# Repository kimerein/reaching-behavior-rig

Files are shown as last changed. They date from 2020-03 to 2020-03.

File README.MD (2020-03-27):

This repo contains hardware and software files for building and operating a behavior rig that dispenses food pellets to a mouse. 
The food pellets are positioned in front of the mouse by an apparatus containing two stepper motors controlled by an Arduino. 
The mouse sits in the "mouse house" or mouse enclosure to access the food pellets. 
There is a gap between the "mouse house" and the mechanism that presents food pellets, so the mouse has to reach for the food pellet with the forelimb and forepaw.
Pellet orientation is not controlled during loading or pellet presentation to the mouse. 
The rig is designed to maneuver 20 mg food pellets. 

# Useful Info. and Answers to FAQs

* **This is for scientists.**
* **This is a behavior rig that presents food pellets to a mouse.**
* **The components of the rig are controlled by an Arduino.**
* **This is for scientists interested in studying forelimb reaching behaviors in mice, designed by a neuroscientist.** 
* **This repo contains materials related to my post-doctoral work.** 
Note: I am a scientist, not an engineer. 
Certainly, there are non-optimal components of this design. 
This is not fancy. Yes, one step is to glue on a paintbrush.
Please feel free to improve upon and share this design, but ...
* **Please acknowledge this Github page in any publications relying on or adapting this design. Thank you!**
* **This is DIY and use-at-your-own-risk material.** 
You will need to adapt the code and designs to your own goals.
I cannot answer support requests.
Building this rig based on these materials requires a decent understanding of Arduino, ThorLabs parts, and generally good spatial reasoning.
* **Known Issues**
This rig works well for my needs. I run this rig for 5 hours per day without jammed pellets. 
However, there are several caveats.
First, the rig does not work well unless all components are exactly properly positioned and very well-secured.
Second, mis-loading of pellets does occur. This occurs for about 1 in 50 pellets (e.g., pellet is not in the proper position when presented to the mouse or pellet is missing).
Third, jammed pellets are infrequent, but this does occur. Usually, I observe jammed pellets only when a screw is loose or a rig component is improperly positioned.
The rig requires periodic maintenance.
Note that commercial food hoppers (pellet dispensers) do exist. 
* **Food pellets**
This rig was designed to dispense 20 mg food pellets from Bio-Serv (e.g., F05301).

# Contributors

https://github.com/kimerein/

https://github.com/marciiadarola/

# Parts List

Only the top 2 sections of this list, "Components for maneuvering pellets" and "Arduino components", contain components required to build the behavior rig.
I use the other components for other features.

[Parts List](./parts_list.csv)

## Notes on 3D-printed parts

These are the 3D-printed parts:

[Pellet loader container](./parts/pellet_loader_container.stl)

[Pellet loader conical piece](./parts/pellet_loader_conical_piece.stl)

[Chute and blocker (these two mechanisms are combined into one piece)](./parts/chute_and_blocker.stl)

[Perch rings to fit around ThorLabs posts](./parts/perch_rings.stl)

[Perch middle piece, where mouse's forepaws rest, should be cut to correct size and fit into 2 perch rings](./parts/perch_connector.stl)

I've also included the .ipt versions of these .stl files, in case you want to modify the designs with CAD.

I printed these pieces using Black V4 resin on a Form 2 FormLabs printer, but other resins and printers should work.

## Notes on laser-cut parts

These are the parts cut out of acrylic sheets, saved as Adobe Illustrator files:

[One file including all of the parts to be cut from 1/8 inch black acrylic](./parts/behaviorBox_with_pellet_presenter.ai)

[Pellet presenter wheel alone](./parts/pellet_presenter_wheel.ai)

[Pellet loader parts to be cut from 1/16 inch clear acrylic](./parts/loader_two_plastic_parts.ai)

Note that the pellet presenter wheel has raster engraving (black filled sections). All other lines indicate clean cuts through the acrylic.

The file [with labels](./parts/behavior_box_parts_with_labels.ai) is not for laser cutting. It is instructional only and includes labels on the pieces.

# Building Reaching Rig

[How to build rig](./BUILDRIG.MD)

# Control code for Arduino

An example of the Arduino code that I use to control the behavior box is in this repo. 
Note that you may need to debug the code with your behavior box.
In particular, be aware that, if Arduino turns on a pull-up resistor, the HIGH and LOW states will be flipped for certain pin outs.

# Instructions

First, you should have a clear understanding of your experimental needs. 
Use these materials as a starting point for finding your own solutions and approach.
You will need to adapt/problem-solve depending on your goals.

# How to Help

In the spirit of open-source science, please publish your own improvements and updates to Github. Happy experimenting!

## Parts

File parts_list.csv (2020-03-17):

Material | Description | Vendor | Part # | # needed | Link
Components for maneuvering pellets:
Bipolar Stepper Motor 200 Step 0.35A 12VDC | stepper motor | Digi-Key | 1528-1062-ND | 2 | https://www.digikey.com/product-detail/en/324/1528-1062-ND/5022791?WT.mc_id=IQ_7595_G_pla5022791&wt.medium=cpc&wt.srch=1
Black Scratch-Resistant Acrylic 24 x 24 inches | black acrylic for laser cutter | McMaster-Carr | 8505K744 | 1 | https://www.mcmaster.com/8505k744-8505K143
Access to 3D printer | 3D printing (see .stl files) | Harvard Instrumentation Core
Access to laser cutter | laser cut black acrylic (see .ai files) | Harvard Instrumentation Core
Ø1/2" Post Holder, Spring-Loaded Hex-Locking Thumbscrew, L = 1.5" | structure | ThorLabs | PH1.5 | 3 | https://www.thorlabs.com/thorproduct.cfm?partnumber=PH1.5#ad-image-0
PH1 - Ø1/2" Post Holder, Spring-Loaded Hex-Locking Thumbscrew, L = 1" | structure | ThorLabs | PH1 | 2 | https://www.thorlabs.com/thorproduct.cfm?partnumber=PH1#ad-image-0
BA1S - Mounting Base, 1" x 2.3" x 3/8" | structure | ThorLabs | BA1S | 5 | https://www.thorlabs.com/thorproduct.cfm?partnumber=BA1S
BA1 - Mounting Base, 1" x 3" x 3/8" | structure | ThorLabs | BA1 | 2 | https://www.thorlabs.com/thorproduct.cfm?partnumber=BA1
DTS50 - 2" Dovetail Translation Stage, 1/4"-20 Taps | structure | ThorLabs | DTS50 | 2 | https://www.thorlabs.com/thorproduct.cfm?partnumber=DTS50
PH2 - Ø1/2" Post Holder, Spring-Loaded Hex-Locking Thumbscrew, L = 2" | structure | ThorLabs | PH2 | 4 | https://www.thorlabs.com/thorproduct.cfm?partnumber=PH2#ad-image-0
TR2 - Ø1/2" Optical Post, SS, 8-32 Setscrew, 1/4"-20 Tap, L = 2" | structure | ThorLabs | TR2 | 7 | https://www.thorlabs.com/thorproduct.cfm?partnumber=TR2
TR1 - Ø1/2" Optical Post, SS, 8-32 Setscrew, 1/4"-20 Tap, L = 1" | structure | ThorLabs | TR1 | 4 | https://www.thorlabs.com/thorproduct.cfm?partnumber=TR1
TR3 - Ø1/2" Optical Post, SS, 8-32 Setscrew, 1/4"-20 Tap, L = 3" | structure | ThorLabs | TR3 | 3 | https://www.thorlabs.com/thorproduct.cfm?partnumber=TR3
PH3 - Ø1/2" Post Holder, Spring-Loaded Hex-Locking Thumbscrew, L = 3" | structure | ThorLabs | PH3 | 1 | https://www.thorlabs.com/thorproduct.cfm?partnumber=PH3#ad-image-0
DC Power 12V 5.5mm Barrel Connector Female To Pigtail Bare Wires | power to monitor, auxiliary motor shield power, camera power | Amazon | B00E0O2BWC | 3 | https://www.amazon.com/Power-Barrel-Connector-Female-Pigtail/dp/B00E0O2BWC
Zip ties |  | general lab supplies
Kwik-Sil | securing motors with help of motor positioners | WPI | KWIK-CAST | 1 | https://www.wpiinc.com/products/top-products/kwik-cast-kwik-cast-sealant
Dental cement | e.g., Metabond | general lab supplies
Fast-drying glue | e.g., Loctite with Zipkicker catalyst | general lab supplies
Arduino project enclosure | securing Arduino | SparkFun | PRT-10088 | 1 | https://www.sparkfun.com/products/10088
Extension cords and power strip |  | general lab supplies
12 V power source | for Arduino, monitor, DVR and V2 motor shield auxiliary power | general lab supplies |  | 4
5 V power source | for camera | general lab supplies |  | 1
MB8 - Aluminum Breadboard 8" x 8" x 1/2", 1/4"-20 Taps | 1 plate for mouse enclosure, 1 plate for pellet presentation apparatus (Note that I decouple these two pieces to prevent transference of motor vibrations to mouse) | ThorLabs | MB8 | 2 | https://www.thorlabs.com/thorproduct.cfm?partnumber=MB8
AP90 - Right-Angle Mounting Plate, 1/4"-20 Compatible | attaches mouse enclosure to translation stage | ThorLabs | AP90 | 2 | https://www.thorlabs.com/thorproduct.cfm?partnumber=AP90
CL2 - Heavy-Duty Variable Height Clamp, 1/4"-20 Tapped | structure | ThorLabs | CL2 | 3 | https://www.thorlabs.com/thorproduct.cfm?partnumber=CL2
XT95P12 or other mounting plate | structure | ThorLabs | XT95P12 | 1 | https://www.thorlabs.com/thorproduct.cfm?partnumber=XT95P12
BA2 - Mounting Base, 2" x 3" x 3/8" | structure | ThorLabs | BA2 | 2 | https://www.thorlabs.com/thorproduct.cfm?partnumber=BA2
1/4-20 and 8-32 screws, washers and nuts |  |  |  | many
DC Power 12V 5.5mm Barrel Connector Female To Pigtail Bare Wires | for connecting powered components, including auxiliary power to Arduino motor shield | Amazon | B00E0O2BWC | 4 | https://www.amazon.com/Power-Barrel-Connector-Female-Pigtail/dp/B00E0O2BWC
Thorlabs 6 mm rods for pellet loader | for positioning pellet loader 3D-printed pieces | Thorlabs | ER6 | 2 | https://www.thorlabs.com/thorproduct.cfm?partnumber=ER6
Thorlabs holder for 6 mm rods | for positioning pellet loader 3D-printed pieces | Thorlabs | CP02B | 2 | https://www.thorlabs.com/thorproduct.cfm?partnumber=CP02B
Clear Cast Acrylic Sheet, 12" x 12" x 1/16" | for pellet loader wheel and bottom piece of pellet loader | McMaster-Carr | 8560K171 | 1 | https://www.mcmaster.com/catalog/125/3732
Princeton Best Synthetic Sable Brush - Round, Short Handle, Size 3 | for brushing off pellets | Blick | Item #:06170-1003 | 1 | https://www.dickblick.com/items/06170-1003/
Arduino components, including components for logging Arduino actions:
Arduino Uno R3 | microcontroller | Adafruit | PID: 50 | 1 | https://www.adafruit.com/product/50
Adafruit V2 motor shield, v2.3 | for controlling 2 stepper motors | Adafruit | PID: 1438 | 1 | https://learn.adafruit.com/adafruit-motor-shield-v2-for-arduino/overview
Proto-Screwshield (Wingshield) R3 Kit for Arduino | for securely attaching in/out | Adafruit | PID: 196 | 1 | https://www.adafruit.com/product/196
Shield stacking headers for Arduino (R3 Compatible) | for stacking shields | Adafruit | PRODUCT ID: 85 | 4 | https://www.adafruit.com/product/85?gclid=EAIaIQobChMIvciagNr31AIVl0sNCh3qLgy1EAQYASABEgL-u_D_BwE
Arduino Ethernet Shield 2 | for writing Arduino output data to micro-SD card during experiment | SparkFun | DEV-11166 | 1 | https://www.sparkfun.com/products/11166
Components for video recording of mouse behavior (30 fps):
Weatherproof TTL Serial JPEG Camera with NTSC Video and IR LEDs | for infra-red (IR) video in behavior box | Adafruit | 613 | 1 | https://www.adafruit.com/product/613
SanDisk microSDHC 32GB Flash Memory Card, Black, SDSDQM-032G-B35 | micro-SD card for Arduino output storage | Amazon | B004G60AD6 | 1 | https://www.amazon.com/SanDisk-microSDHC-Memory-SDSDQM-032G-B35-Packaging/dp/B004G60AD6
SanDisk 32GB Ultra Class 10 SDHC UHS-I Memory Card Up to 80MB, Grey/Black (SDSDUNC-032G-GN6IN) | SD card for video storage | Amazon | B0143RT8OY | 1 | https://www.amazon.com/SanDisk-Ultra-Class-Memory-SDSDUNC-032G-GN6IN/dp/B0143RT8OY?s=pc
Anysun® Mini Security DVR - Sd Card Recording with Remote Control Sd Slot | DVR for storing video on SD card | Amazon | B00WUPKLPW | 1 | https://www.amazon.com/Anysun%C2%AE-Mini-Security-DVR-Recording/dp/B00WUPKLPW
LEE Filters 3x3" Infra Red #87C Infrared Polyester Filter | for ensuring that only IR light (not red light) exits IR LEDs -- mouse cannot see IR | BandH | B&H # LE87C33 | 1 | https://www.bhphotovideo.com/c/product/292664-REG/LEE_Filters_87CP3_3_x_3_Infrared.html
N-BK7 Plano-Convex Lens, Ø1", f = 150.0 mm, Uncoated | for camera | ThorLabs | LA1433 | 1 | https://www.thorlabs.com/thorproduct.cfm?partnumber=LA1433
Black and red wires | wiring electronics
Other (optional):
X-mini WE micro portable NFC Bluetooth smartphone capsule speaker, XAM17-GM-B | play sound of motors turning all the time, to mask actual motor turning | Amazon | B00I6BJ592 | 2 | https://www.amazon.com/X-mini-portable-Bluetooth-smartphone-XAM17-GM-B/dp/B00I6BJ592
Liztek 40W/8A 5-Port USB Charger Desktop Charger Charging Station with SmartLiz Technology (Black) | for charging speakers | Amazon | B00R6MJ7UO | 1 | https://www.amazon.com/Liztek-Charger-Charging-SmartLiz-Technology/dp/B00R6MJ7UO?s=kitchen
UGREEN 3.5mm Male to Female Extension Stereo Audio Extension Cable Adapter Gold Plated Compatible for iPhone, iPad or Smartphones, Tablets, Media Players | audio to speakers | Amazon | B00LM4OMUW | 1 | https://www.amazon.com/UGREEN-Extension-Adapter-Compatible-Smartphones/dp/B00LM4OMUW
Belkin Speaker and Headphone Splitter | audio to speakers | Amazon | B000067RC4 | 1 | https://www.amazon.com/Belkin-Speaker-and-Headphone-Splitter/dp/B000067RC4?th=1
Camecho Universal 7 inch Car Vehicle RearView reversing color Monitor 2 Video Input & High Resolution Rotating TFT LCD Screen with Remote Control and Mounting Bracket | for watching mouse in behavior rig, in real-time | Amazon | B00MQF9P12 | 1 | https://www.amazon.com/Camecho-Universal-RearView-reversing-Resolution/dp/B00MQF9P12?s=electronics
Interlock magnetic switch | for determining when behavior rig door is open | Amazon | B0009SUF08 | 1 | https://www.amazon.com/Directed-Electronics-8601-Magnetic-Switch/dp/B0009SUF08
Velcro Tape 3/4"Wx15' Sticky Back Black Boxed | for attaching acoustic foam to inside of behavior box | Amazon | B01MTKKG33 | 1 | https://www.amazon.com/Velcro-Tape-Sticky-Black-Boxed/dp/B01MTKKG33?s=office-products
Custom machined headframe holders |  | Harvard Machine Shop |  | 1 pair
Optional: components for optogenetics, including manipulator for fiber placement, wire to BNC, etc. |  | general lab supplies
Blue LED and resistor | LED distractor | general lab supplies
Black tape |  | general lab supplies
99% Blackout Window Curtain Panel Grommet Top Drapes 2 Panel Set Room Darkening Thermal Insulated Blackout Drapes for Bedroom (W52 x L84,Black) | for covering behavior box during behavior (mouse needs to be completely in the dark) | Amazon | B01N0T12O6 | 1 | https://www.amazon.com/Blackout-Curtain-Grommet-Darkening-Insulated/dp/B01N0T12O6?s=furniture
Magnetic Latch for 1" and 1-1/2" High Aluminum T-Slotted Framing Extrusion | holding door closed | McMaster-Carr | 47065T165 | 1 | https://www.mcmaster.com/#catalog/123/1948/=1a31q14
Rail-to-Panel Hinge for 1" High Rail, Black OR 201590 Sea-Dog Line Offset Butt Hinge Stainless Steel 1-1/2" X 1-1/2" Inch | hinge for behavior box door | McMaster-Carr or Amazon | https://www.mcmaster.com/47065t162 OR B00U1TJOZC | 2 pairs | https://www.amazon.com/201590-Sea-Dog-Line-Offset-Stainless/dp/B00U1TJOZC | https://www.mcmaster.com/47065t162
Optional: Clay for blocking light from exiting fiber (if doing optogenetics)
Optional: rotary encoders for measuring wheel positions
Optional: NogaFlex Holder - Model: NF1022 | Flexible arm for positioning optical fiber for optogenetics, for positioning air tubing | Amazon | B002NERHSO | 1 | https://www.amazon.com/Noga-NogaFlex-Holder-Model-NF1022/dp/B002NERHSO?s=industrial
Optional: 8 inch ThorLabs post holder for positioning Noga arm | For holding Noga arm
FC/FC General Purpose POF Patch Cords, 1.00 m 1.0 mm plastic optical core, polyethylene 2.2 mm jacket, 1.00 m | for optogenetic stimulation of superficial cortical regions | Industrial Fiber Optics | IF 181L-1-0 | 1 or more | http://i-fiberoptics.com/patchcord-detail.php?series=181L&stock_number=IF%20181L-1-0&summaryrow=12
316 Stainless Steel Dowel Pins | for raising behavior rig and adding pellet collecting drawers | McMaster-Carr | 97395A616 | 4 | https://www.mcmaster.com/#standard-dowel-pins/=1ac8p06
Ø1.5" Mounting Post, 1/4"-20 Taps, L = 1" | for raising behavior rig and adding pellet collecting drawers | Thorlabs | P1 | 4 | https://www.thorlabs.com/thorproduct.cfm?partnumber=P1
Rail aluminum T-slotted framing extrusion, triple profile | 24 inches | McMaster-Carr | 47065T511 | 3 | https://www.mcmaster.com/47065t511
Rail aluminum T-slotted framing extrusion, single profile | 24 inches | McMaster-Carr | 47065T101 | 7 | https://www.mcmaster.com/47065t101
Aluminum T-slotted framing extrusion, 6 inch brace | 6 inches, 1 inch thick | McMaster-Carr | 47065T186 | 12 | https://www.mcmaster.com/47065t186
Rail aluminum T-slotted framing extrusion, single profile, cut-to-length OR cut the length yourself | 28 inches | McMaster-Carr | 47065T801 | 4 | https://www.mcmaster.com/47065t801
Corner flush 90 deg angle surface bracket for single rails | smallest size | McMaster-Carr | 3136N157 | 10 | https://www.mcmaster.com/3136n157
Drop-in fasteners | spring-loaded for staying in place in vertical rails | McMaster-Carr | 47065T226 | 20 | https://www.mcmaster.com/47065t226
Snap-in mounting plate | for holding black acrylic coverings | McMaster-Carr |  | 9
Egg crate sound-proofing | 3 inches thick, 54 x 54 inches | McMaster-Carr | 9710T66 | 3 | https://www.mcmaster.com/9710T66
Sensor holder drop-in fastener | spring-loaded | McMaster-Carr | 5537T352 | 10 | https://www.mcmaster.com/5537t352
Black acrylic | 24 x 24 inches | McMaster-Carr | 8505K744 | 5 | https://www.mcmaster.com/8505k744-8505K143
Black Cast Acrylic Sheet 24" x 36" x 1/8" | 36 x 48 inches | McMaster-Carr | 8505K745 | 1 | https://www.mcmaster.com/8505k745-8505K153
Full Size Clear Polycarbonate Food Pan - 2 1/2" Deep | for collecting dropped food pellets underneath the behavior rig | WebstaurantStore | 700PLPA8002 | 2 | https://www.webstaurantstore.com/full-size-clear-polycarbonate-food-pan-2-1-2-deep/700PLPA8002.html

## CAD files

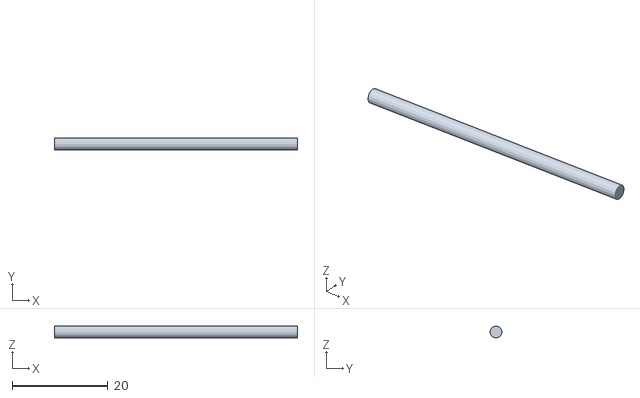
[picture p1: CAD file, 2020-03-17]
parts/perch_connector.stl
50.8 x 2.50 x 2.50

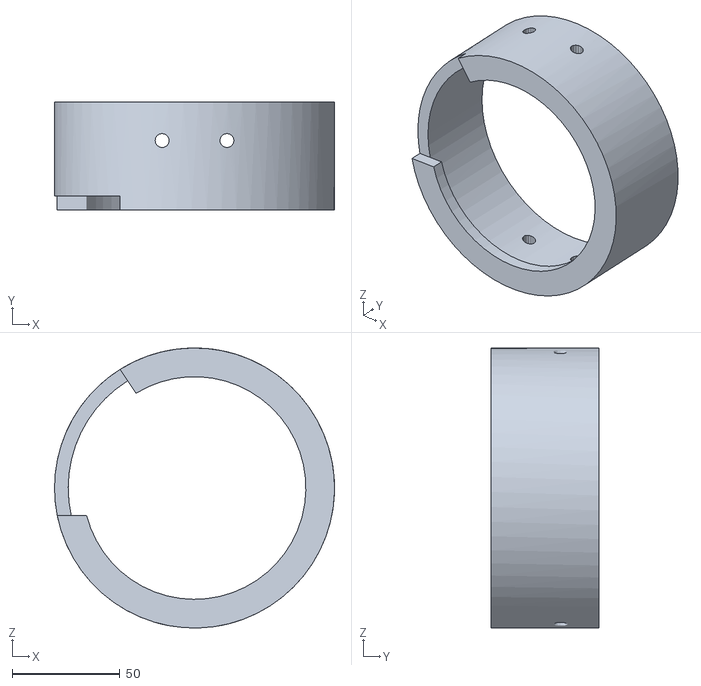
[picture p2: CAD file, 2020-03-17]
parts/pellet_loader_container.stl
129.7 x 49.8 x 129.7

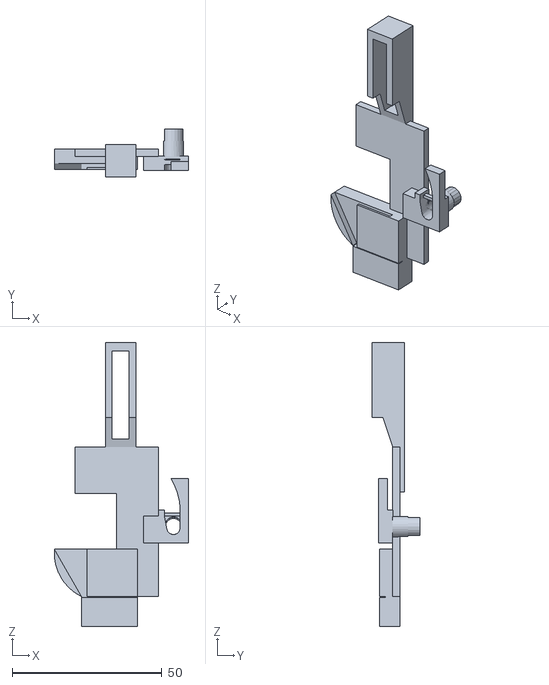
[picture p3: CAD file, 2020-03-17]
parts/chute_and_blocker.stl
44.9 x 16.2 x 94.9

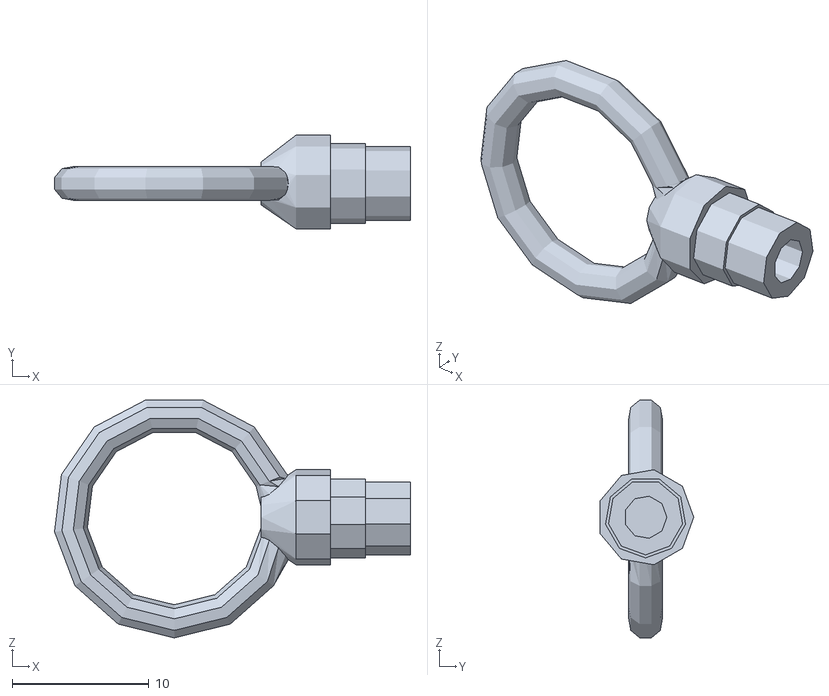
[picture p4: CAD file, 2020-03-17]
parts/perch_rings.stl
26.0 x 6.85 x 17.4

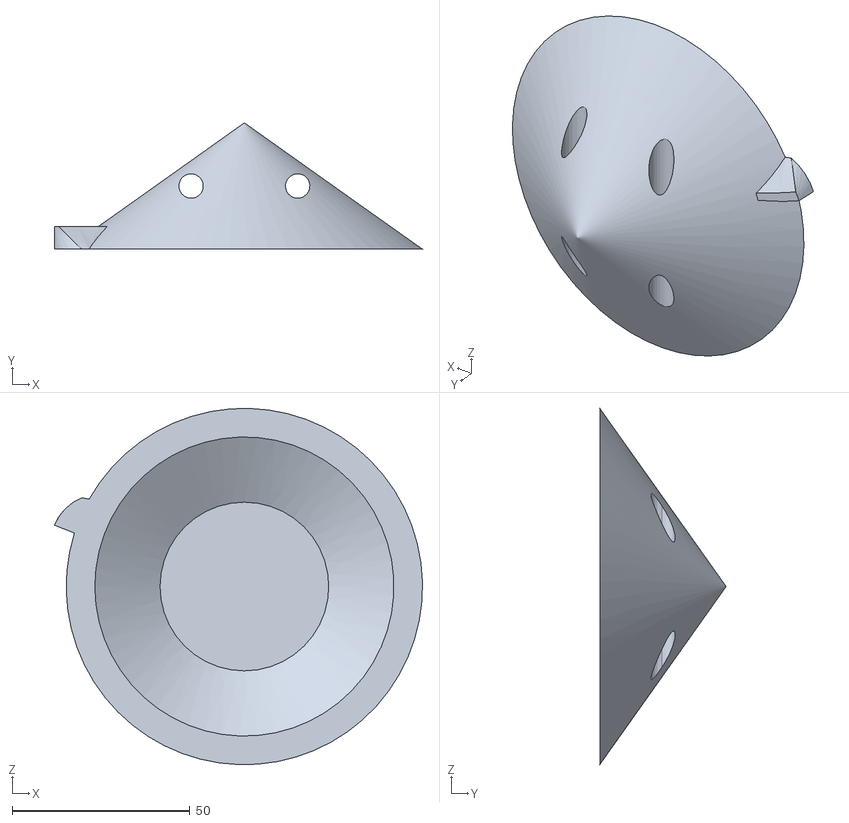
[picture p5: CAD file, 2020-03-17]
parts/pellet_loader_conical_piece.stl
103.6 x 35.6 x 100.2

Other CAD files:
parts/chute_and_blocker.ipt
parts/pellet_loader_conical_piece.ipt
parts/pellet_loader_container.ipt
parts/perch_connector.ipt
parts/perch_rings.ipt

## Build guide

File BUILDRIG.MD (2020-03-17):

# Building Reaching Rig

1. Build frame (McMaster Aluminum T-Slotted Framing Extrusion, see Materials List for sizes). 
2. 3D print .stl files. I used Black V4 resin with a FormLabs 2 printer, but other printers and resins should work.
3. Laser cut .ai files. Note that the pellet presenter wheel has raster engraved sections (black fill). For all other lines (red), cut all the way through the acrylic sheet.
4. NOTE: Build the two halves of the behavior rig separately. We will then attach these two pieces to the box frame. Build: A. Pellet Disks Apparatus and B. Mouse House Apparatus on two separate breadboards. (This separation prevents transmission of the stepper motor vibrations to the mouse.) Optional: 3rd micrometer for up-down movement of mouse. Note that this rig could be built excluding all the micrometers (to save money), but I prefer to include at least 2 micrometers to increase positioning flexibility. 
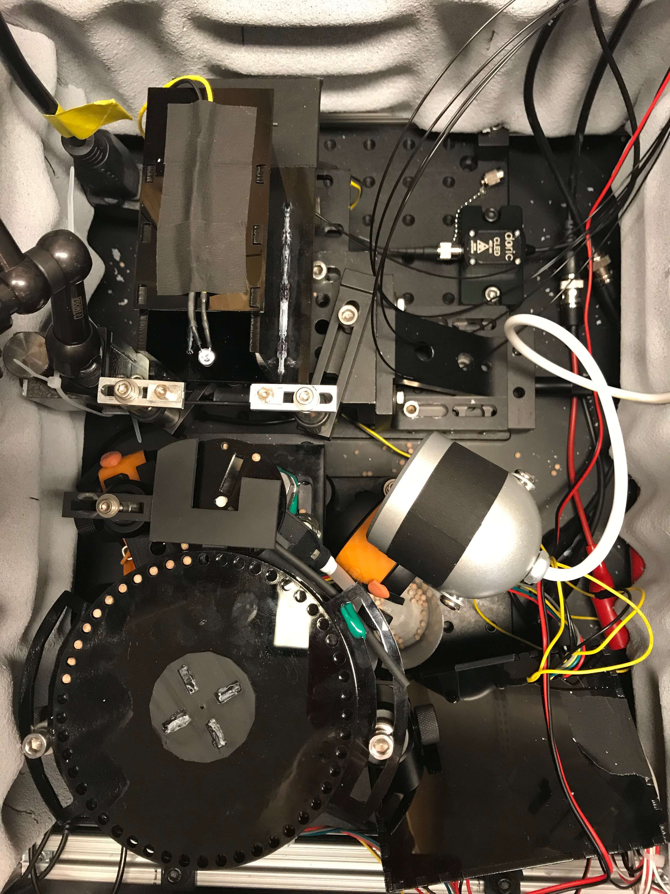
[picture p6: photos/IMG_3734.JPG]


[Two halves of rig from above](./photos/IMG_3734.JPG)

5. **BUILD PELLET DISKS APPARATUS**
6. Assemble raised micrometer platforms. Use appropriate Thorlabs posts and post holders to ensure that the height of Pellet Disks Apparatus matches the height of Mouse House Apparatus. 
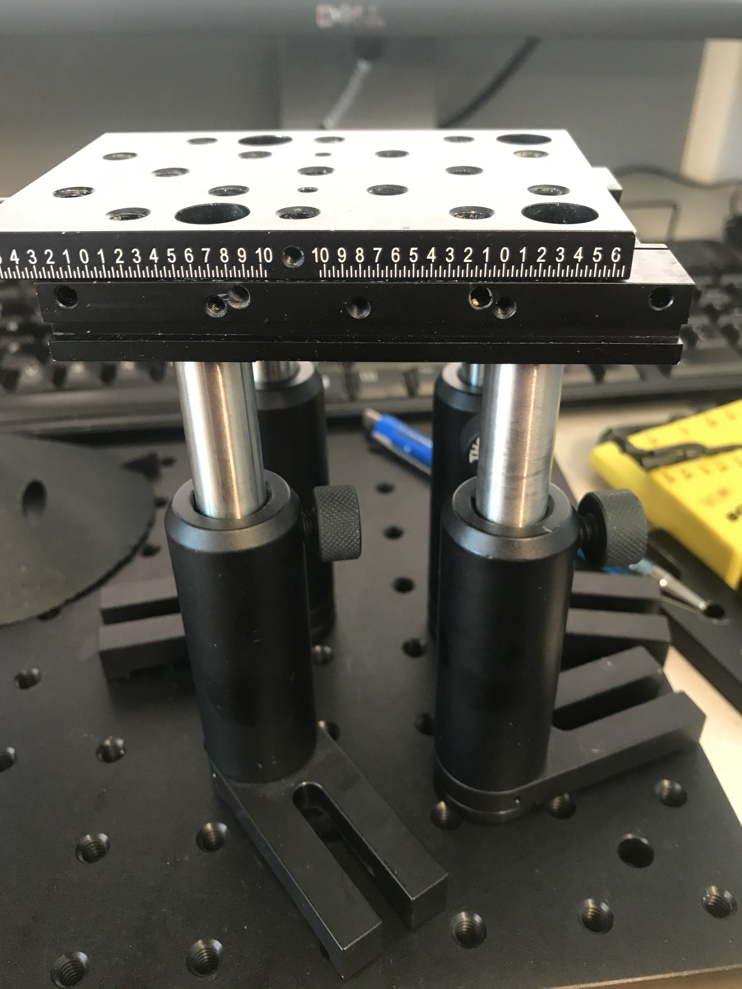
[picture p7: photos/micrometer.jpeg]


[Raised micrometer](./photos/micrometer.jpeg)

7. Build mechanism to present food pellets. These plastic disks maneuver the food pellets. (Think: lazy susan.) There are 2 circular plastic disks. Each is secured to a stepper motor, which enables the disk to spin. The first (smaller) disk presents food pellets to the mouse. The second (larger) disk loads food pellets onto the first (smaller) disk. I call this first disk the “pellet presenter wheel”, and I call the second disk the “loader wheel”. Attach each circular disk to the top of a stepper motor shaft: Hold the plastic disk in place with quick-drying glue (e.g., Loctite/Zipkicker catalyst), then further secure this attachment for permanent hold using dental cement. There is a 3D-printed piece that  mates the “loader wheel” (plastic disk with 50 holes around the edge) to the stepper motor shaft. The “loader wheel” (plastic wheel) sits on the top of this 3D-printed piece. 
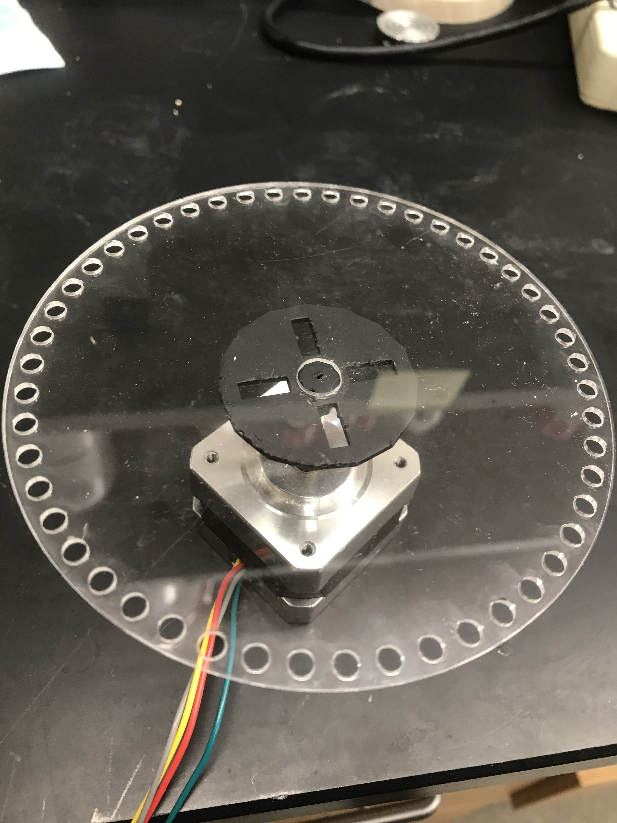
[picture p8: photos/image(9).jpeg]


[Stepper motor, then 3D-printed piece, then loader wheel ](./photos/image(9).jpeg)

The “pellet presenter wheel” should sit directly on top of the motor shaft. Use a leveler to be sure that each wheel is mounted approximately flat with respect to the bottom of the stepper motor base. 

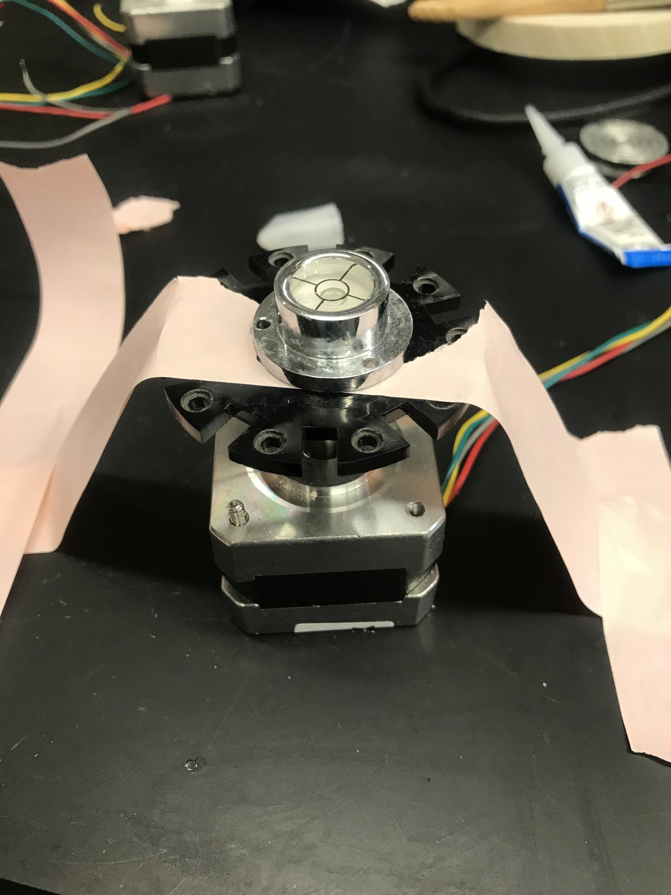
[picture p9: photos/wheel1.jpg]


[Upright attachment method](./photos/wheel1.jpg)

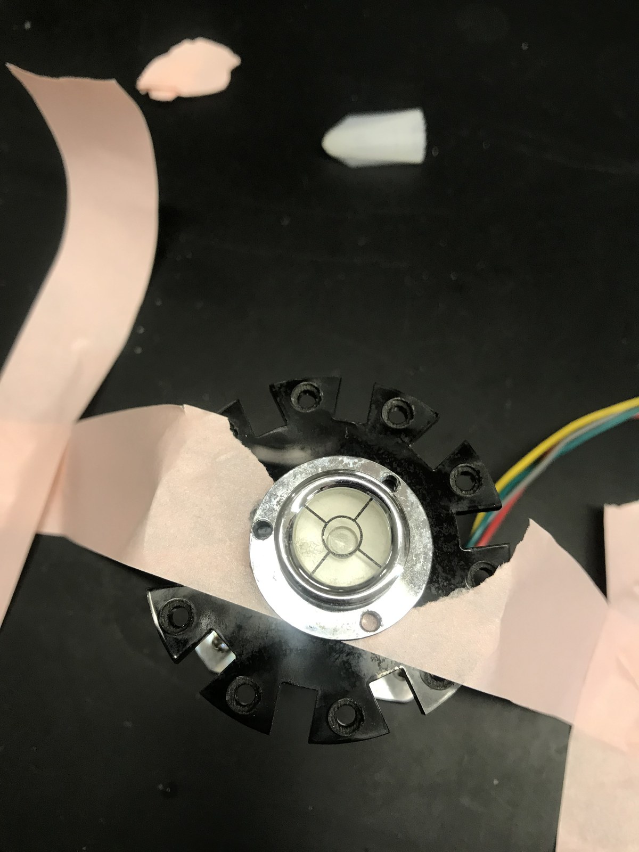
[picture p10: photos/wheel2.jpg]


[Level wheel](./photos/wheel2.jpg)

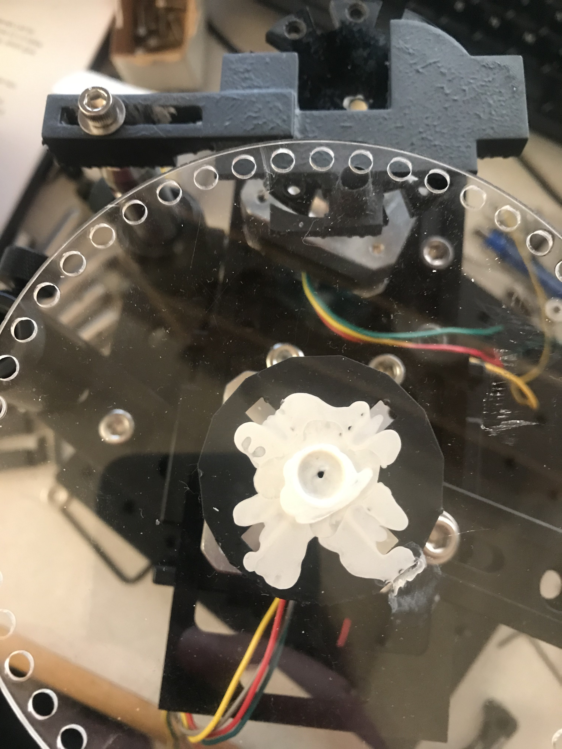
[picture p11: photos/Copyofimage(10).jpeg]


[Pellet loader wheel from above](./photos/Copyofimage(10).jpeg)

8. Use plastic “motor positioners” (plastic stencils) to correctly position the stepper motors on top of the micrometers. Place one motor positioner (black plastic cut-out) on top of the micrometer and screw down loosely. 
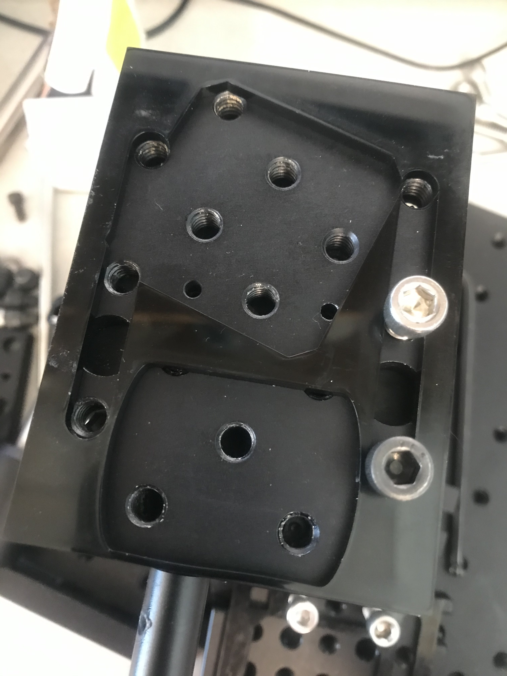
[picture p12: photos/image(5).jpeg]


[“Motor positioner” on micrometer](./photos/image(5).jpeg)

The stepper motor attached to the pellet presenter wheel will sit in this front-most stencil. Attach a small, compatible Thorlabs plate (I used XT95P12, but you can use any compatible piece) to the back of the micrometer, and place the second motor positioner (plastic stencil) on this back plate.

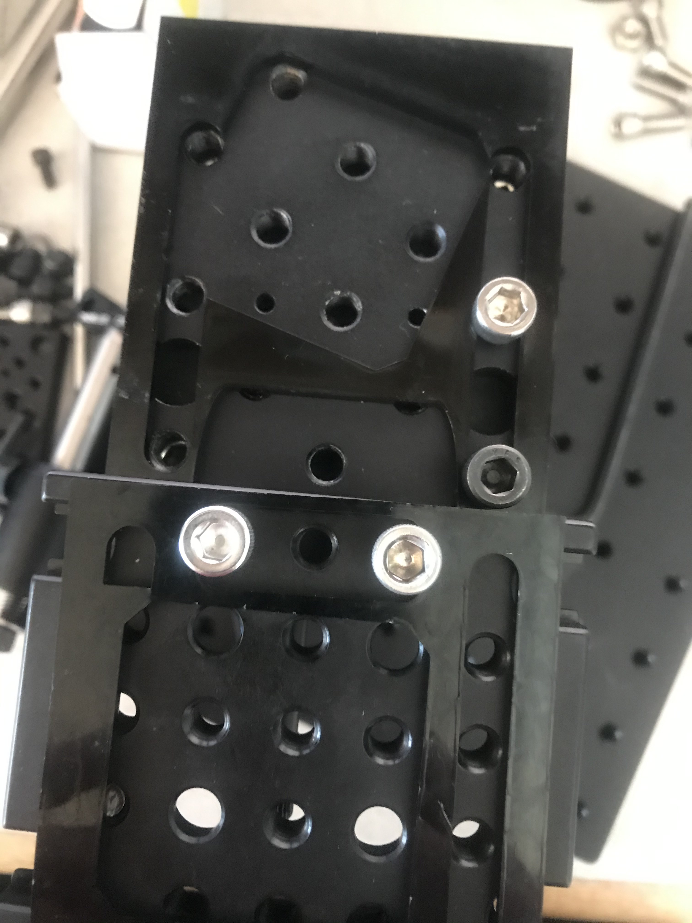
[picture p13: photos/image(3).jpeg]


[Plate and motor positioner for pellet loader](./photos/image(3).jpeg)

The stepper motor attached to the pellet loader sits in this back stencil. Loosely secure motor positioners to the micrometer platforms using screws. Place the stepper motors in the motor positioners.

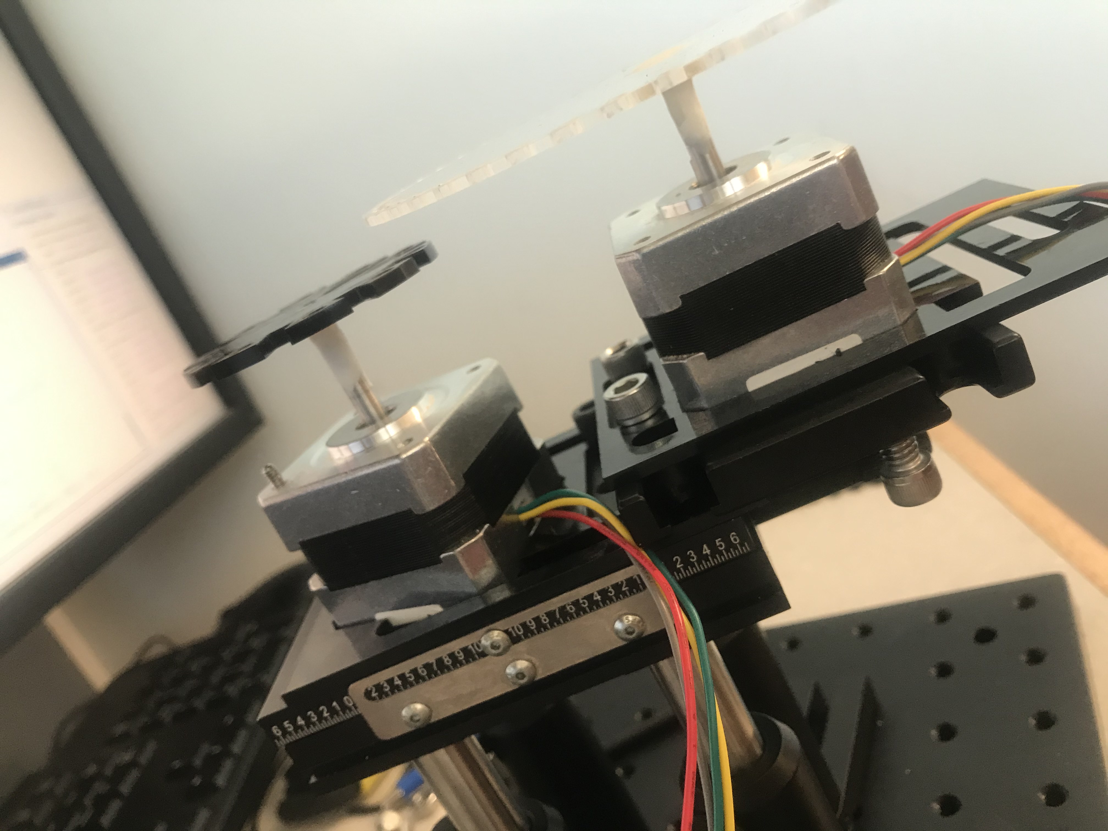
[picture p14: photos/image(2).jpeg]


[With motors](./photos/image(2).jpeg)

9. Gently move the “motor positioners” (plastic stencils) to move the stepper motors. Align the two wheels: a hole in the pellet loader wheel should be aligned directly above a hole in the pellet presenter wheel. 
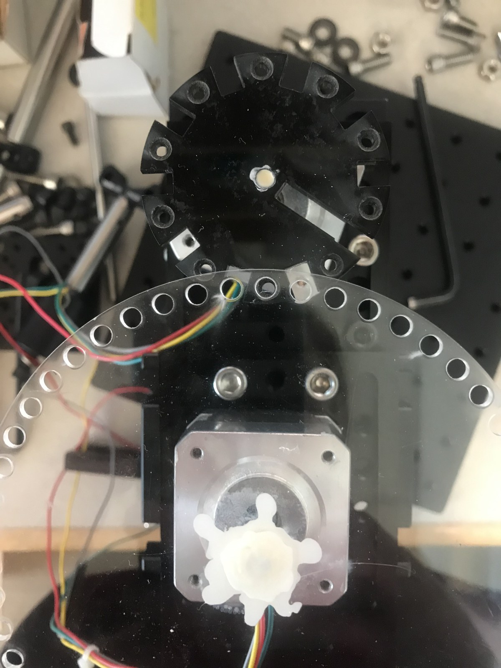
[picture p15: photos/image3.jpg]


[Aligned](./photos/image3.jpg)

Tighten screws. (We will need to adjust this again after plugging in the motors.) Be sure to use screw lengths that do not impede micrometer movements.

10. Build the pellet loader. 

   a. Stack these pieces inside of the large, 3D-printer pellet loader container, in this order: plastic ring with one hole 
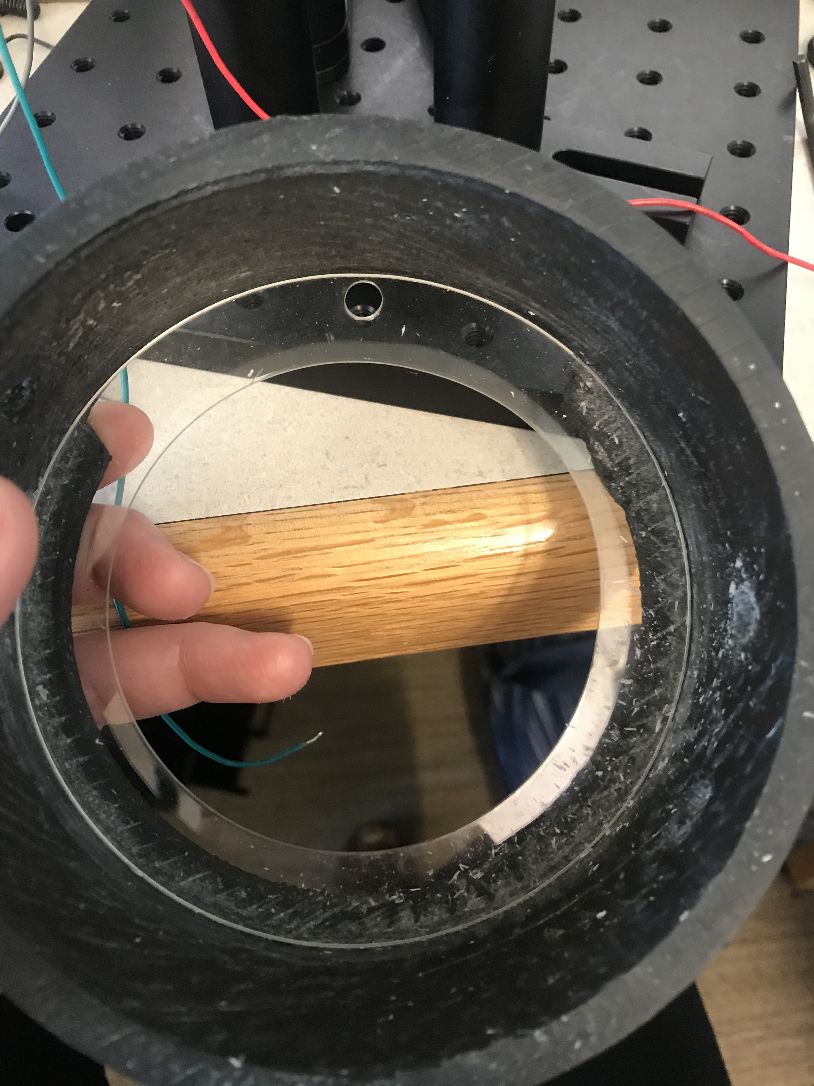
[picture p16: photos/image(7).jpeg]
   

   [here](./photos/image(7).jpeg),

   stepper motor with loader wheel
 
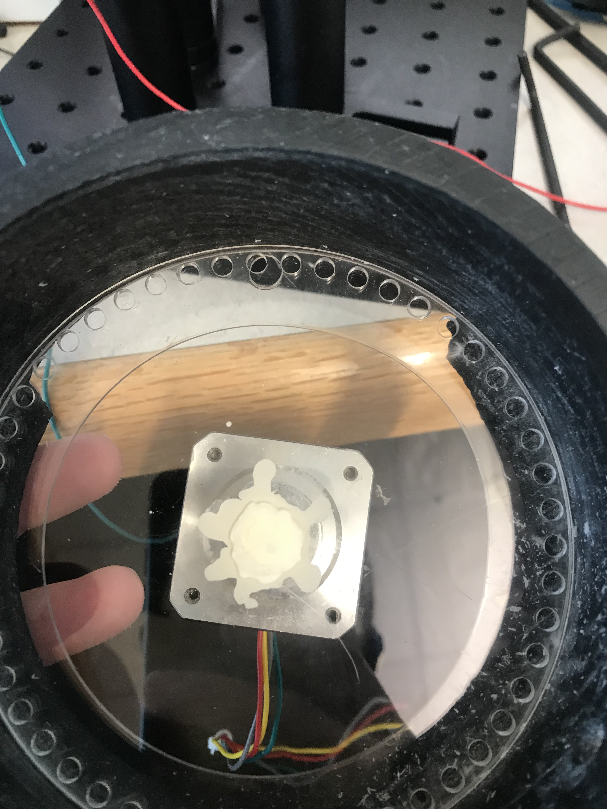
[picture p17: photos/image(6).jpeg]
   

   [here](./photos/image(6).jpeg),

   conical 3D-printed piece

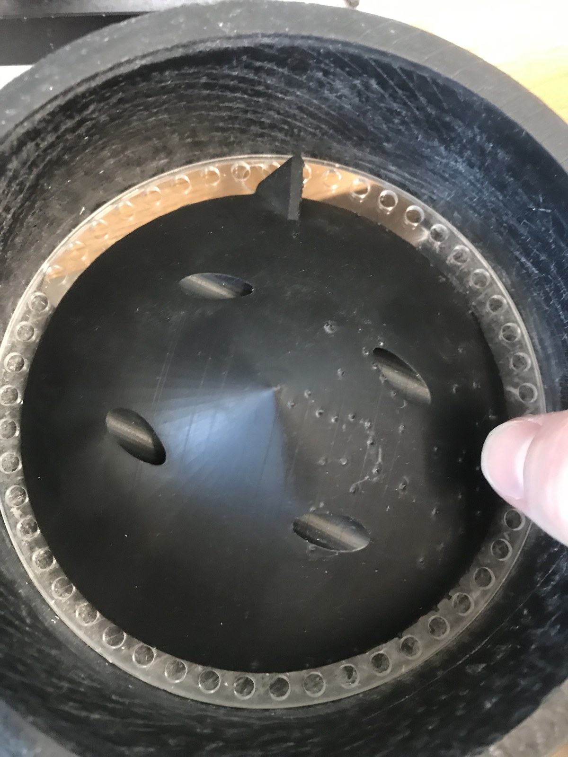
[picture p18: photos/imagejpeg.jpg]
   

   [here](./photos/imagejpeg.jpg).

   b. Put 6 mm rods through the holes in the two 3D-printed pieces to connect them. 

   c. Put the ends of the 6 mm rods into 2 CP02B pieces. 

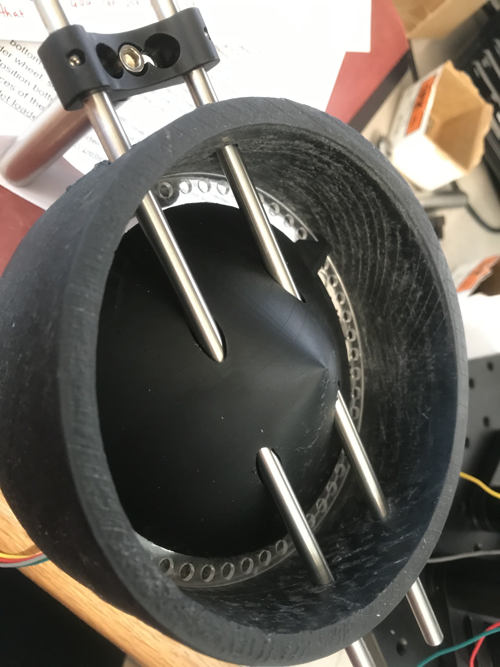
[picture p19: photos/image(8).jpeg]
   

   [Rods and one CP02B](./photos/image(8).jpeg)

   Attach the CP02B to Thorlabs posts. (I used a 1.5 inch post and a 2 inch post.) Set this assembly aside.
   
   d. Attach Thorlabs post holders to Thorlabs base BA1, and attach Thorlabs base BA1 to the back plate that supports the pellet loader wheel. Do this on both sides.
   
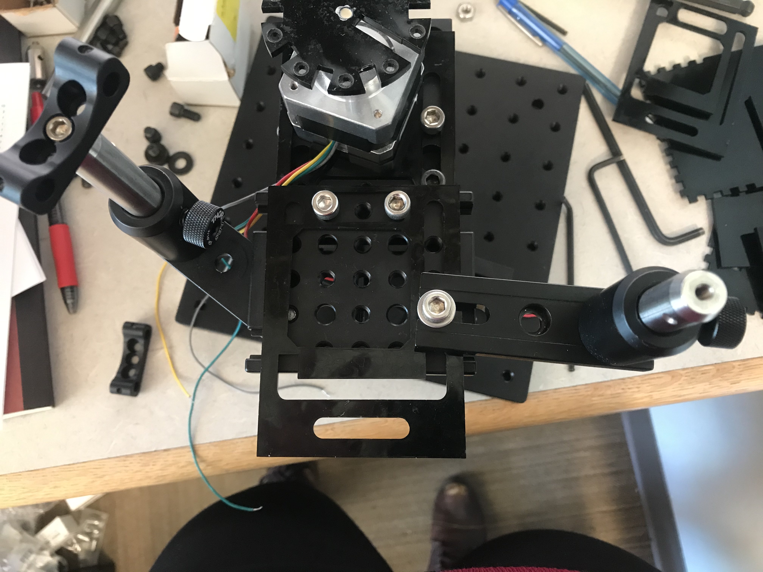
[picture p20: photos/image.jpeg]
   

   [view 1](./photos/image.jpeg)

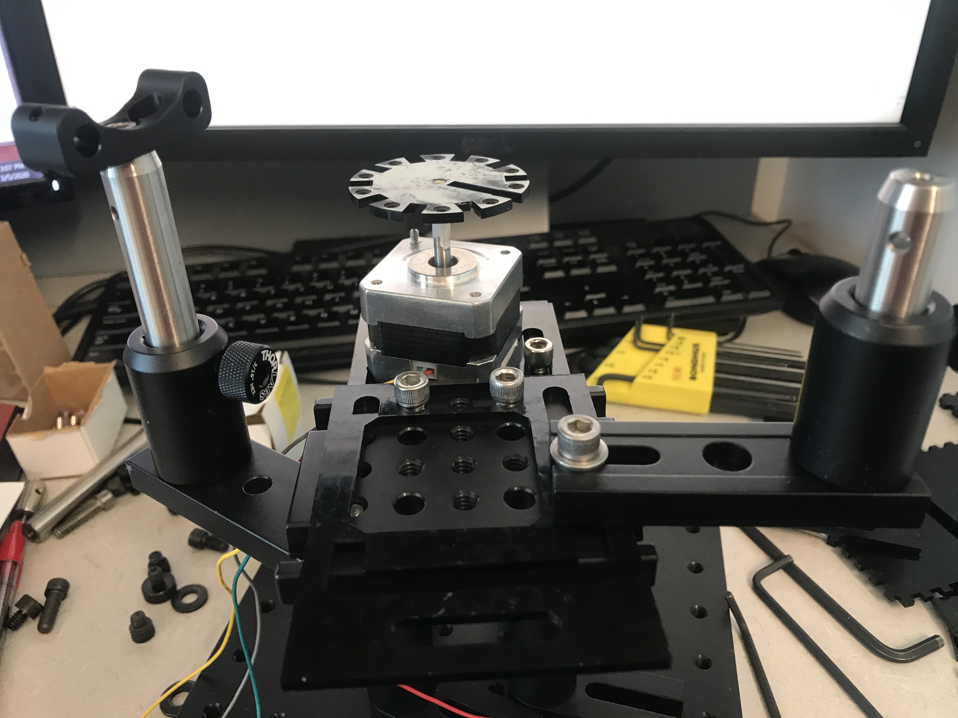
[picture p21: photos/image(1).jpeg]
   

   [view 2](./photos/image(1).jpeg)

   e. Place the assembly from step 10c into the post holders. Note that these post holders now control the height of the pellet loader container.
   
   f. Adjust all pieces so that the stepper motor attached to the pellet loader wheel sits in the motor positioner/stencil. 
   
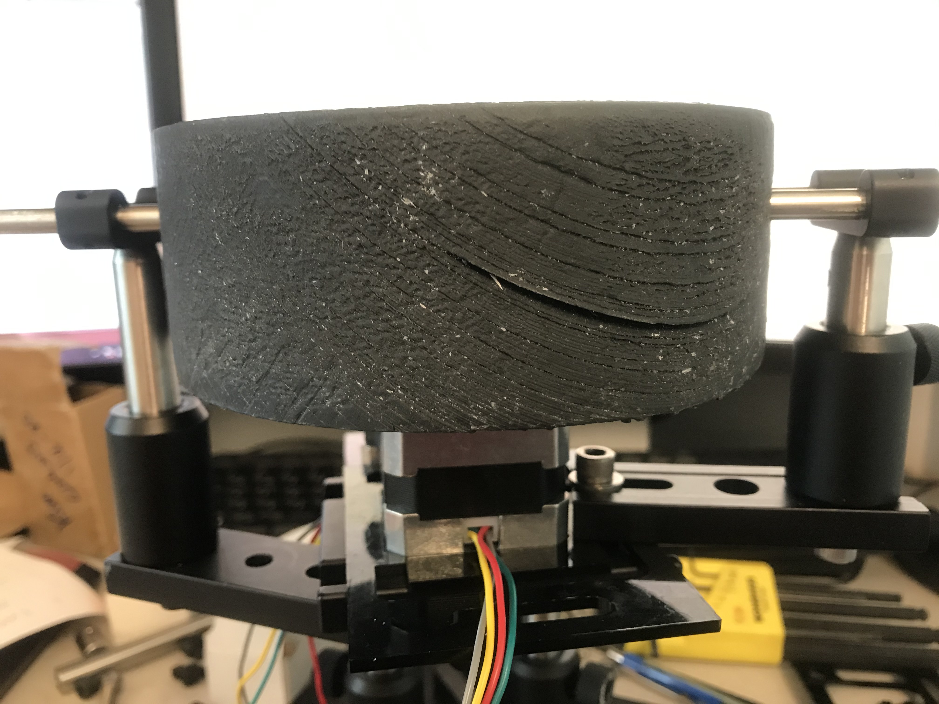
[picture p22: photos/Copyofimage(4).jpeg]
   

   [Pellet loader assembled](./photos/Copyofimage(4).jpeg)

11. Add the pellet chute/blocker. 
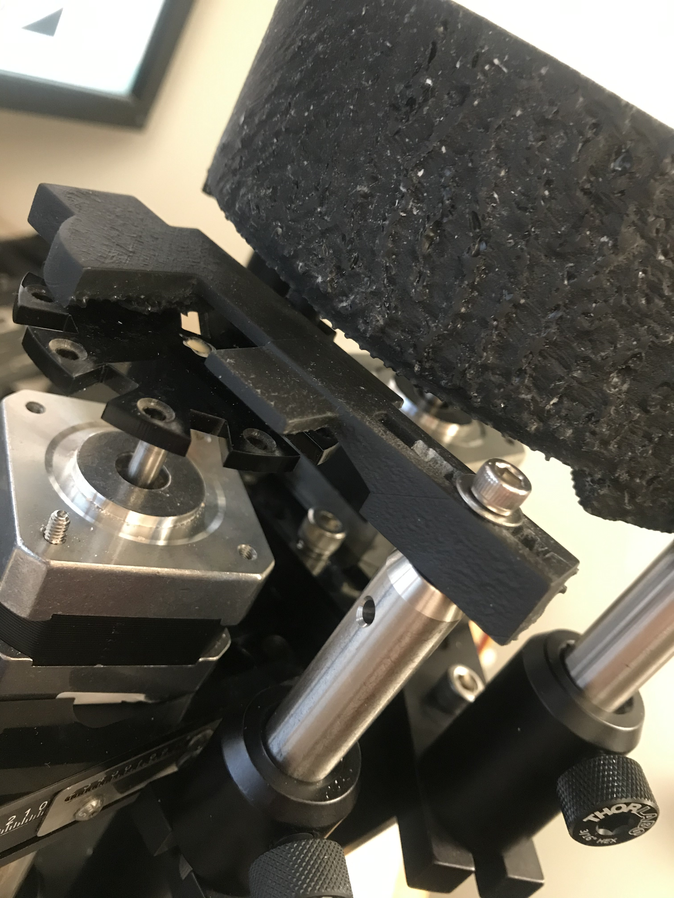
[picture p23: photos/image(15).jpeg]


[Chute/blocker sitting on pellet presenter wheel](./photos/image(15).jpeg)

This is a 3D-printer piece with 2 components. The chute directs pellets out of the loader onto the pellet presenter wheel. 

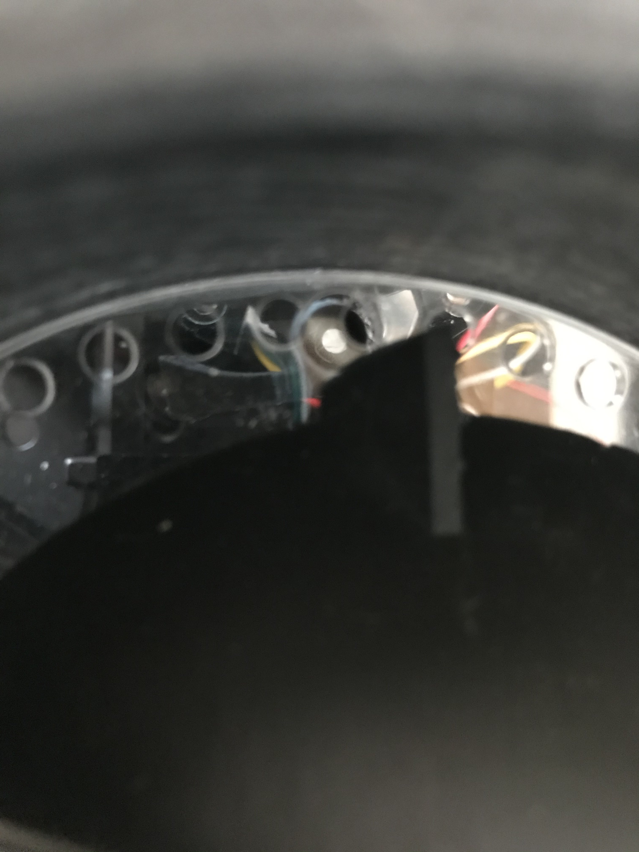
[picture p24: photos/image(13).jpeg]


[Chute sits in the hole in the bottom plastic piece of the pellet loader](./photos/image(13).jpeg)

The blocker knocks off pellets after several turns of the pellet presenter wheel. 

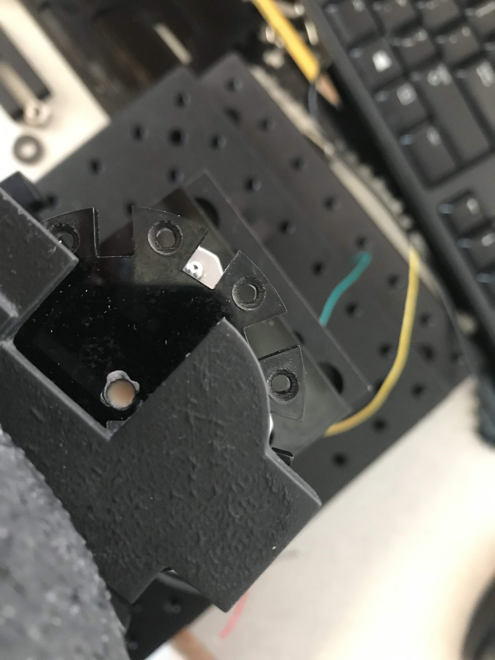
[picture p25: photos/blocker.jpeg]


[Blocker](./photos/blocker.jpeg)

Set up a base (BA1), post holder and post to hold up the chute/blocker. 

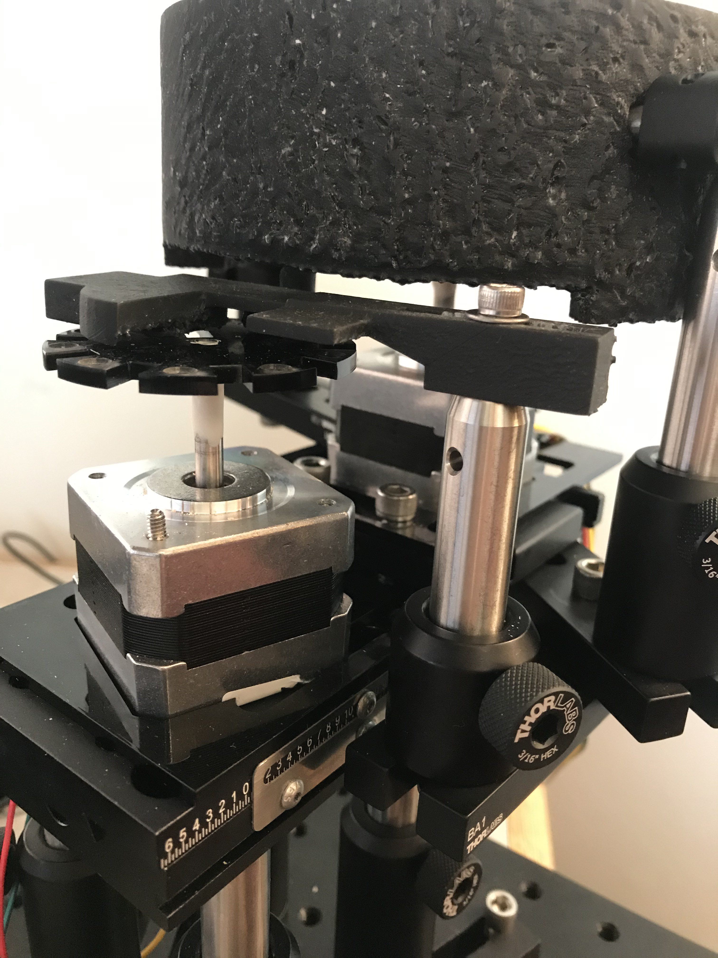
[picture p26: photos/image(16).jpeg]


[Post and post holder to position chute/blocker](./photos/image(16).jpeg)

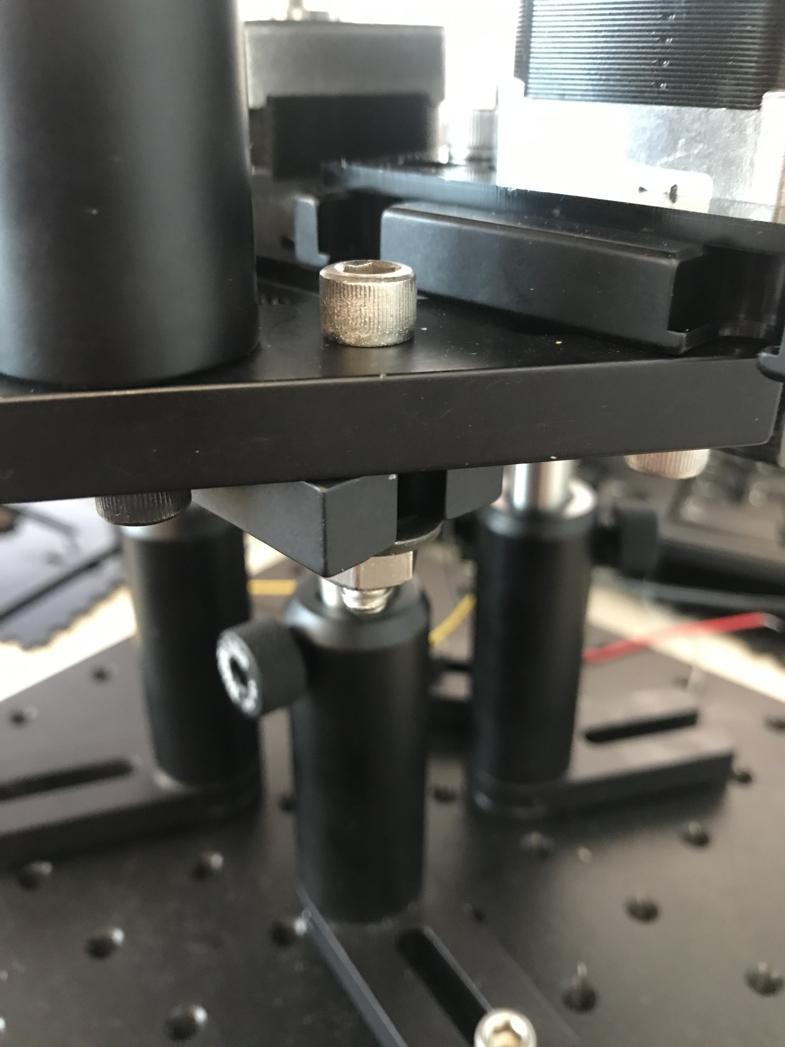
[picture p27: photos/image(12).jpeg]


[Attach BA1](./photos/image(12).jpeg)

Angle this base toward the front-side of the pellet presenter wheel, near the mouse. Insert a screw through the slot in the chute/blocker to loosely hold the chute/blocker in place. This post now controls the height of the chute/blocker. 

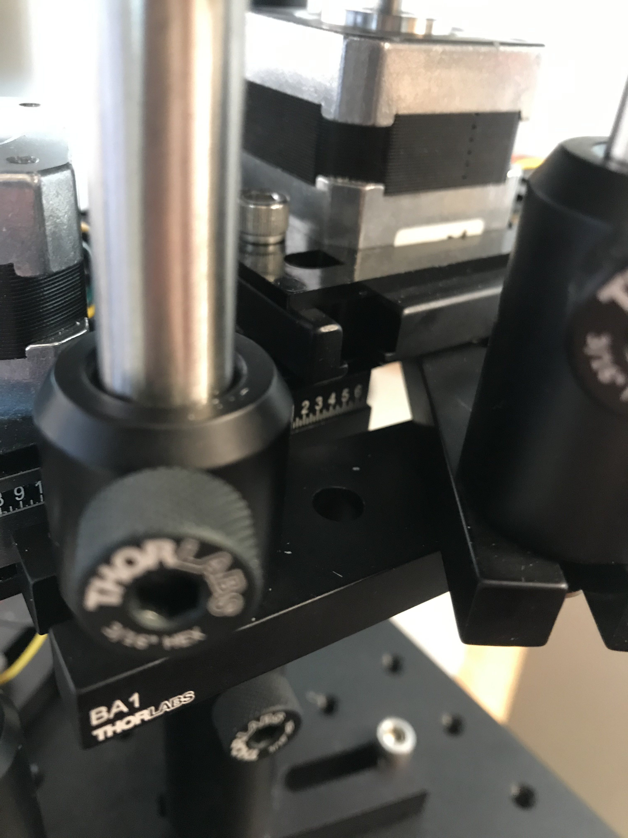
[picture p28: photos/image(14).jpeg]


[Post holder](./photos/image(14).jpeg)

12. Add a mechanism for securing the other side of the chute/blocker. The chute/blocker needs to be very secure in order to properly knock off pellets sitting in the recessed holes of the pellet presenter wheel. Attach BA1S to the micrometer
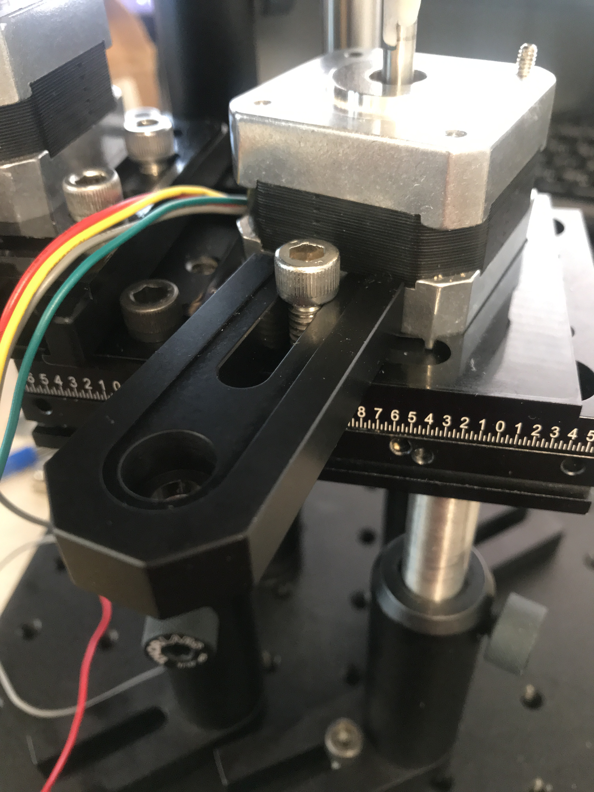
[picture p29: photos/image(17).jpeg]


[here](./photos/image(17).jpeg),

then attach a post holder and post with another BA1S or other base at the top (later, I switch to BA1 for the top piece, but various pieces will work). (I used a 2 inch post.) This base piece sits on top of the chute/blocker

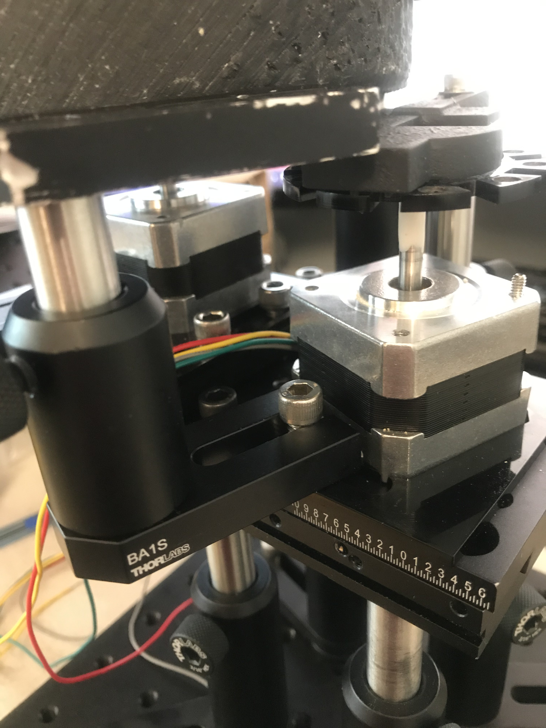
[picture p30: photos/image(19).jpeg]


[here](./photos/image(19).jpeg).

We will glue the base piece to the chute/blocker, once all positioning is finalized. This prevents the blocker from moving as pellets repeatedly hit the side of the blocker.

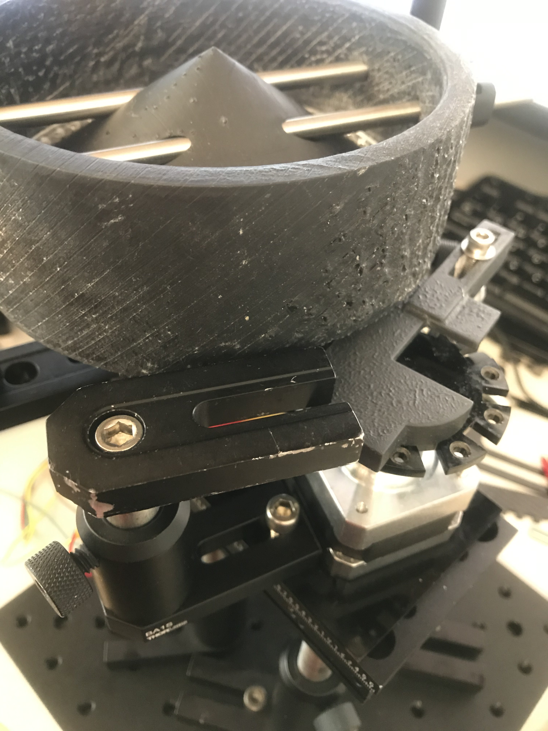
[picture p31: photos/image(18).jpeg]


[Another image from above](./photos/image(18).jpeg)

13. Stack Arduino shields.
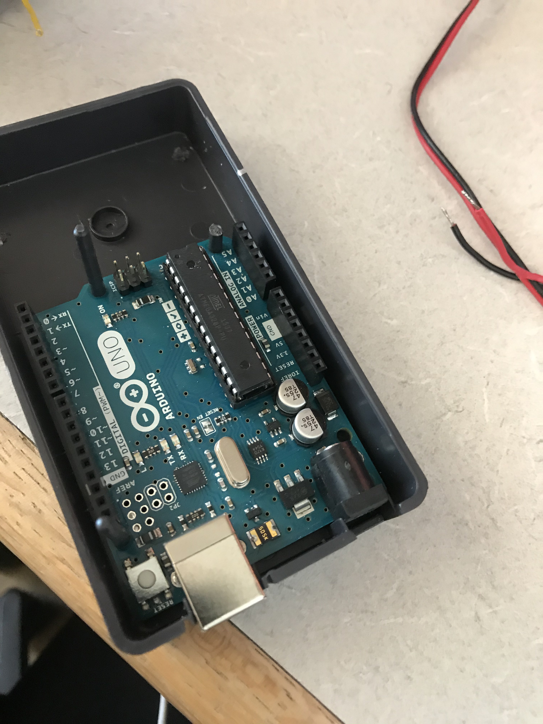
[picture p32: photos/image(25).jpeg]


[Stack 1](./photos/image(25).jpeg)

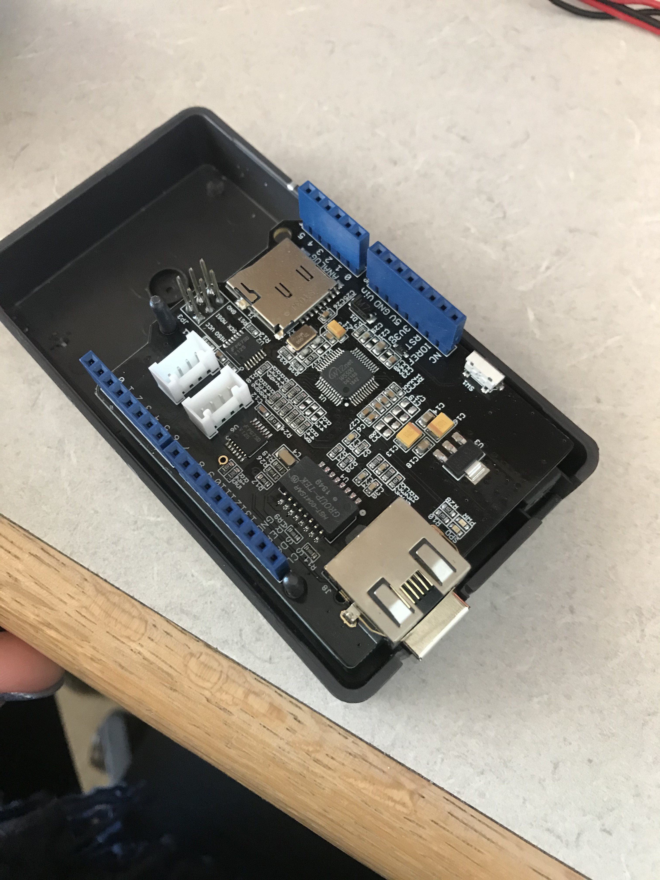
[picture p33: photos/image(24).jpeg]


[Stack 2](./photos/image(24).jpeg)

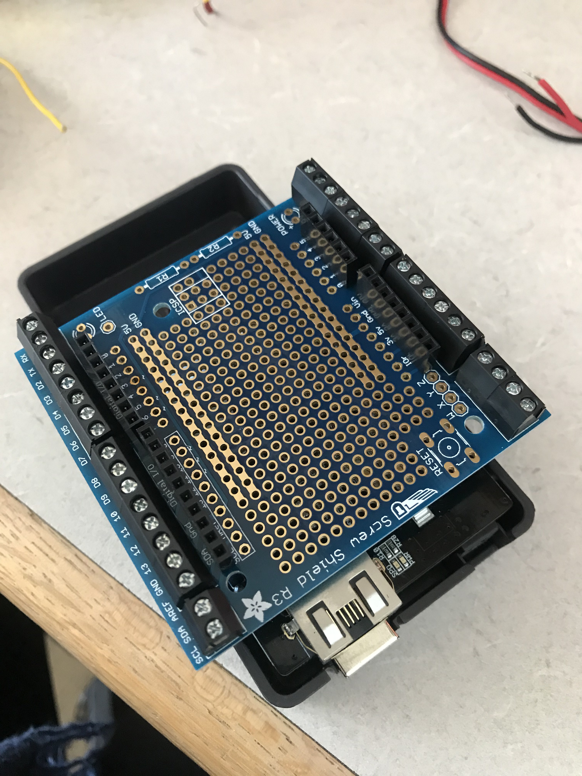
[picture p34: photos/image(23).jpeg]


[Stack 3](./photos/image(23).jpeg)

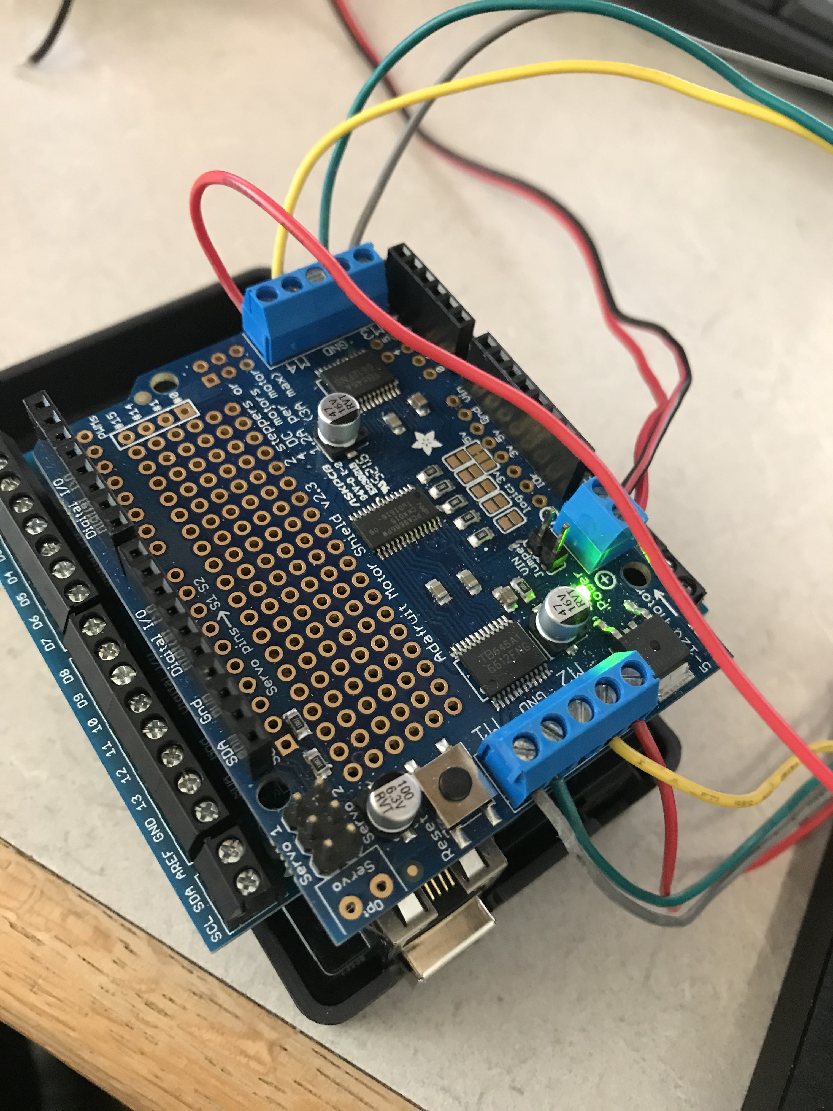
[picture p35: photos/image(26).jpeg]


[Stack 4](./photos/image(26).jpeg)

(In my code, the pellet presenter wheel goes to M3 / M4 of Arduino V2 motor shield, and the pellet loader wheel goes to M1 / M2 of Arduino V2 motor shield.)

14. Adjust positions of all components. Critical step! Position pellet loader wheel, pellet presenter wheel, and the chute/blocker, all with respect to each other. Note that correct positioning of these components is vital to proper rig function.

   a. First, notice that the stepper motors have preferred step positions (i.e., angles). (To see this, wire up auxiliary power to Arduino motor shield, plug a motor into the Arduino motor shield, and make the motor step forward. Motor will only step to certain angles.) Be sure that you are positioning the pellet loader wheel and the pellet presenter wheel with the stepper motors at positions that are allowed when the motors are plugged in.
   
   b. My design assumes that both stepper motors turn clockwise.
   
   c. Let me explain how pellet loading works. 1) Pellets in the fifty holes of the pellet loader wheel are moved toward the lip of the 3D-printed conical piece
   
   

   [here](./photos/image(13).jpeg).

   Only one pellet can fit below the lip of this 3D-printed piece, which prevents more than one pellet from loading at a time. 2) The pellet that fits below this lip falls through the chute onto a recessed hole of the pellet presenter wheel.
   
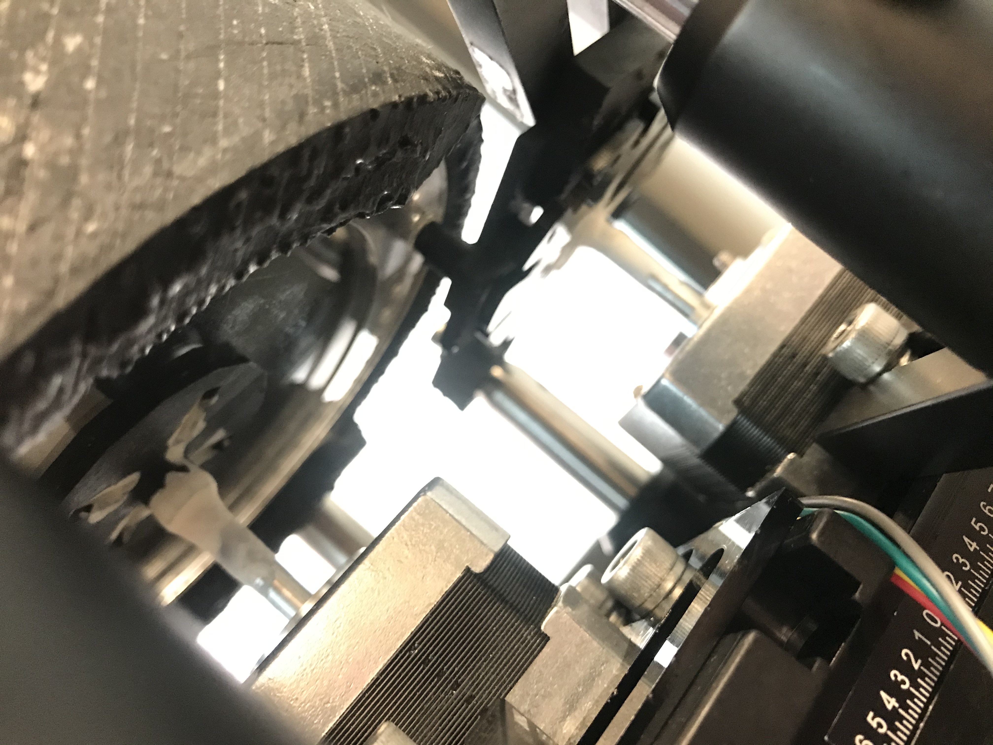
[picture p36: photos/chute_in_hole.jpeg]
   

   [Chute situated in the hole of the bottom plastic piece in pellet loader](./photos/chute_in_hole.jpeg)
   3) The pellet presenter wheel turns, moving the pellet away from the loading position. A new recessed hole of the pellet presenter wheel now sits below the chute. 4) The pellet loader wheel turns again, loading a pellet through the chute. 5) If pellets are not grabbed by the mouse, after 5 to 6 turns of the pellet presenter wheel, the pellets will be knocked off by the blocker. Accomplishing this without errors requires that all rig components be properly positioned. Be patient. Getting everything right takes a little time.
   
   d. The next adjustments should be made after the motors are plugged into the Arduino motor shield, so that we can see how the motors turn and move pellets through the apparatus.
   
   e. First, align pellet presenter wheel with the pellet loader wheel. Get the two holes and the chute lined up. Be sure that these holes are beneath the lip of the 3D-printed piece. At the same time, be sure that the blocker is secured in a position where a turn of the wheel will cause the pellets to hit the curve of the blocker on a trajectory approximately tangent to the blocker
   [for example](./photos/Smooth.MOV).
   Secure all relevant components.
   
   f. Second, set the height of the chute/blocker. Use the two posts on either side to control the height of the chute/blocker. We want the bottom of the chute/blocker to just be touching the top of the pellet presenter wheel.
   
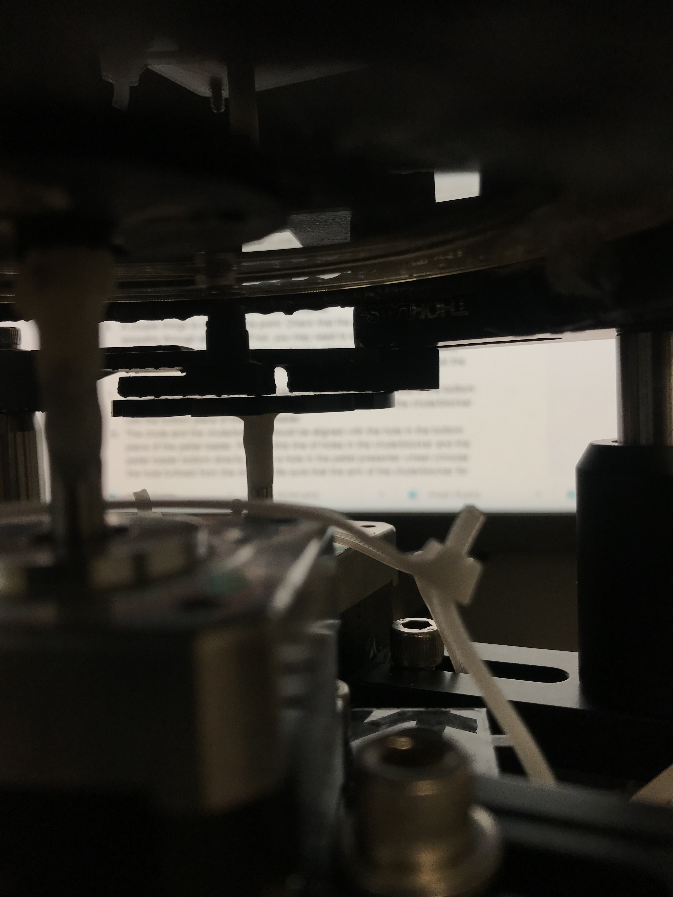
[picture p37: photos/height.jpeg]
   

   [Height of chute/blocker](./photos/height.jpeg)

   g. Third, set the height of the pellet loader container with respect to the pellet loader wheel. Place some pellets into the loader wheel. 
   
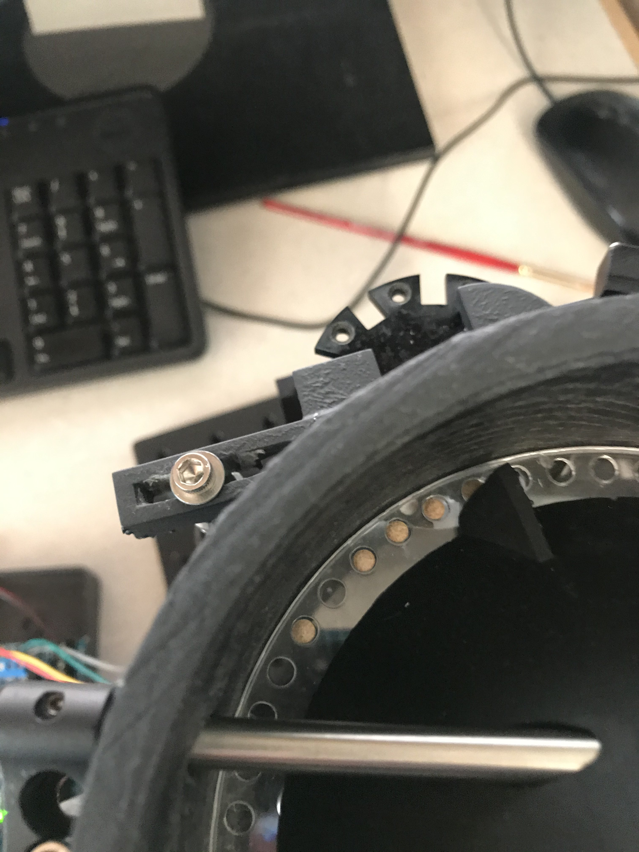
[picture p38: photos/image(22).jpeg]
   

   [Here](./photos/image(22).jpeg)

   The height of the pellet loader container can be adjusted using the side posts. The bottom plastic piece with one hole should be at a height where pellets just sit in the holes, and the top of each pellet is flush with the top of the plastic pellet loader wheel. Rotate the wheel containing pellets to be sure that the height is correct at all angles.
   
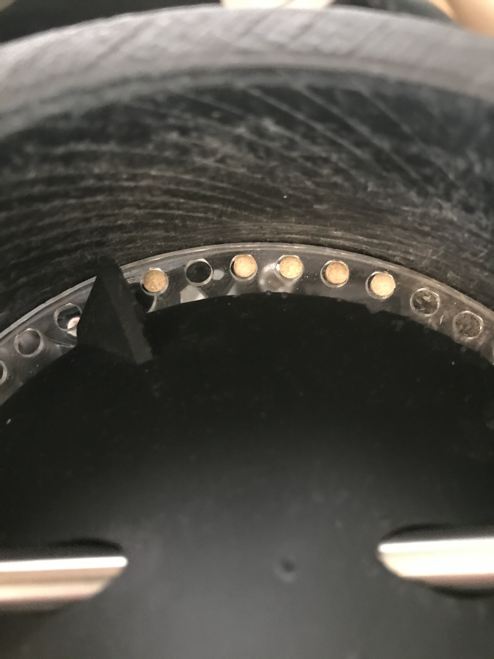
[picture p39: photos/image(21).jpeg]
   

   [Pellets rotated](./photos/image(21).jpeg)

   We don’t want the pellets to slip between the two plastic pieces. Be sure that the pellets slide just under the lip of the 3D-printed conical piece. Once the heights are correct, secure the bottom plastic piece (with one hole) to the large, 3D-printed pellet loader container using Loctite and Zipkicker (I prefer to use this glue, because it can be easily chipped away using needle-nose pliers if a mistake is made).
   
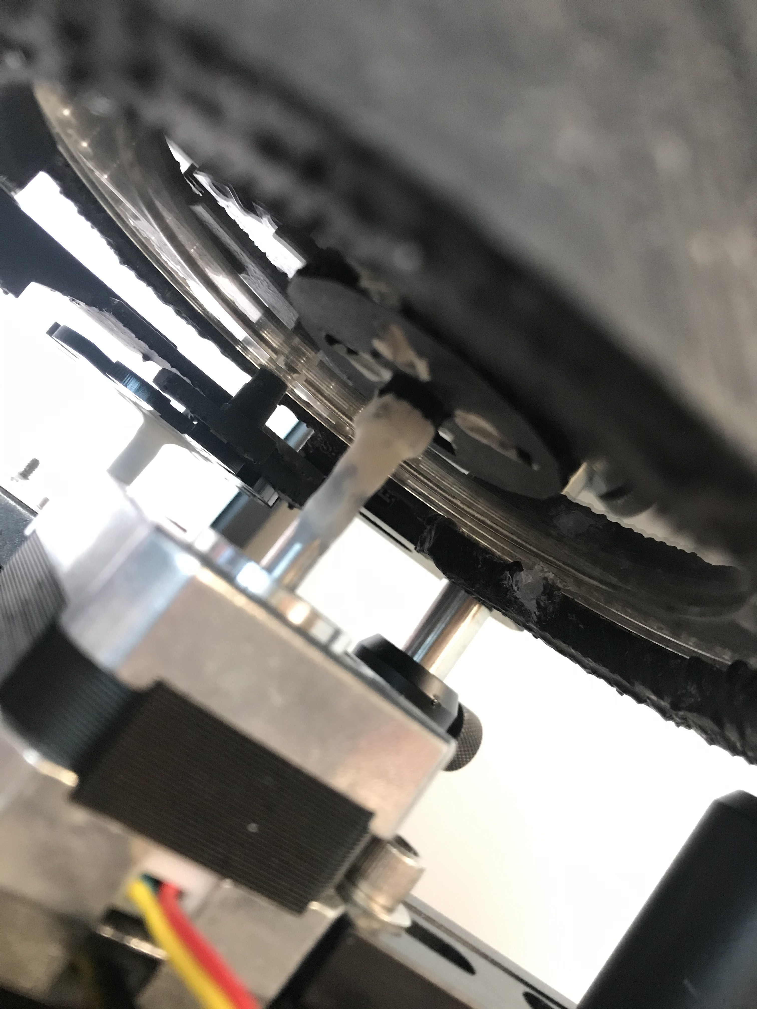
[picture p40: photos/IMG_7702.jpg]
   

   [Glue tacks plastic piece to loader container](./photos/IMG_7702.jpg)

   h. Use clay to secure the position of the conical, 3D-printed piece along the rails. I like to use clay, because the piece can be moved in case of a jammed pellet.
   
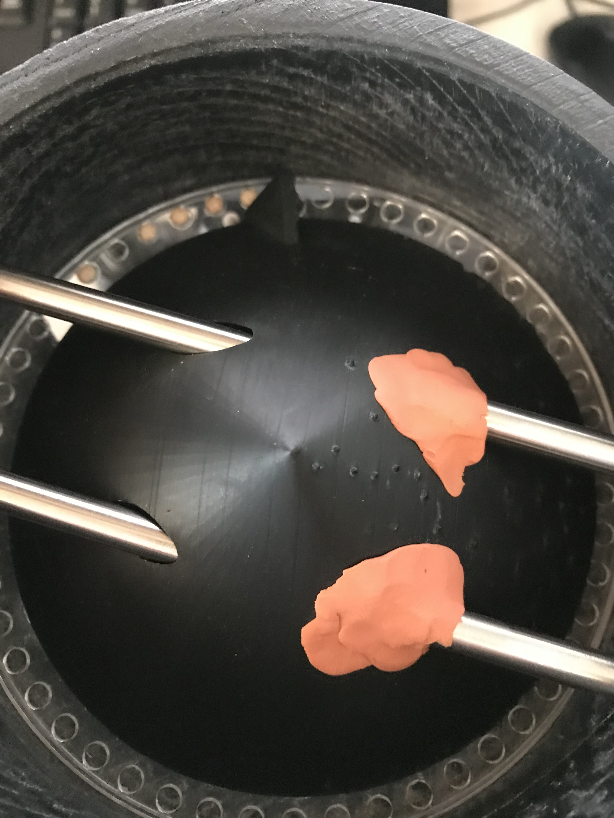
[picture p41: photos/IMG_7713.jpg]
   

   [Clay to hold conical 3D-printed piece](./photos/IMG_7713.jpg)

   There is not much force in this direction along the rails, so clay is sufficient to hold the 3D-printed conical piece in place.
   
   i. Plug in the motors and have the pellet presenter wheel turn many times. Be sure that each hole is beneath the chute. Once you are happy with the position of the pellet presenter wheel’s stepper motor, use Kwik-Cast between the stepper motor and the motor positioner to prevent the motor from rotating side-to-side. 
   
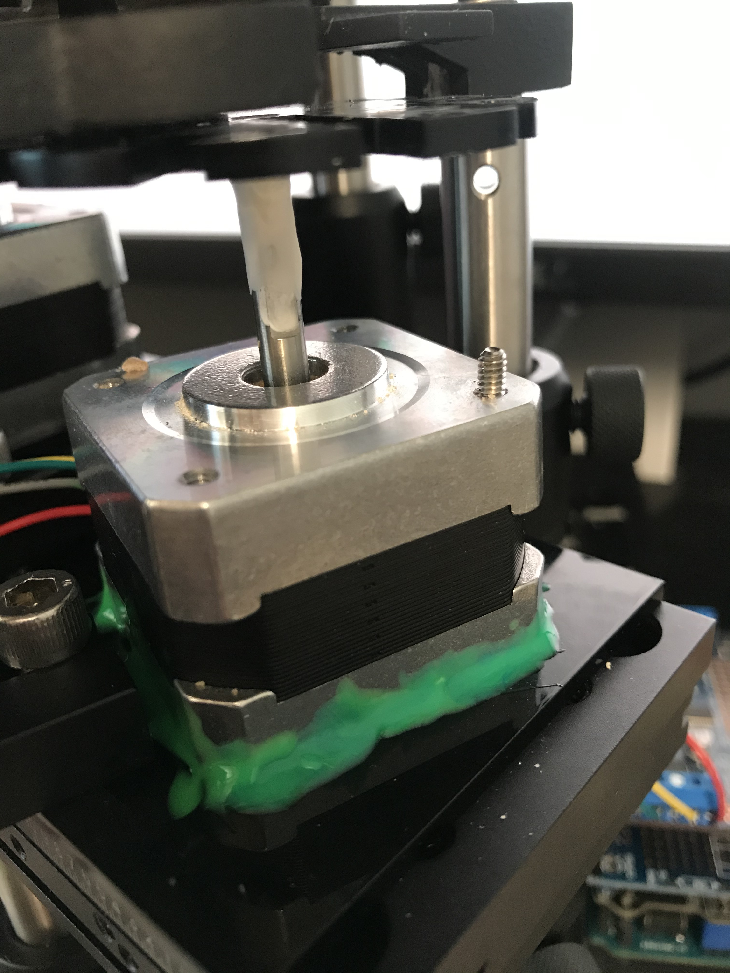
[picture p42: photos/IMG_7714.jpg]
   

   [Kwik-Cast is the green stuff](./photos/IMG_7714.jpg)

   Also, use zip ties to hold down the motor. Be sure that the position of the zip ties does not get in the way of a reasonable range of micrometer movements.
   
   

   [Note zip ties](./photos/height.jpeg)

   j. Zip tie the pellet loader wheel to the back plate. After this, you may need to readjust the height of the pellet loader container.
   
   k. A couple things to check at this point: Remove power to the stepper motors, and turn the wheels manually. Check that the pellet loader wheel moves smoothly through all angles. If not, you may need to slightly readjust the position of the outer 3D-printer pellet loader container. Check that the pellet presenter wheel moves smoothly through all angles. If not, you may need to readjust the height of the chute/blocker. 

   [Smooth movement of wheel through all angles](./photos/IMG_7716.mov)

   l. Now, let’s turn on the motors and load pellets. Here we are checking that pellets are loaded properly from the loader onto the pellet presenter wheel, and also we are checking that the blocker knocks off pellets.
   
   m. Adjust the position and height of the chute/blocker, so that pellets are smoothly knocked off the wheel by the blocker. Remove power to the stepper motors, so that you can turn the wheels manually and find an optimal position for the blocker.
   
   [Example of bad height/pellets jamming](./photos/Jamming.MOV)
   
   [Example of good position and height/pellets removed smoothly](./photos/Smooth.MOV)
   
   n. Now we will add the final component to ensure smooth removal of the pellets from the pellet loader wheel. I use a paintbrush.
   
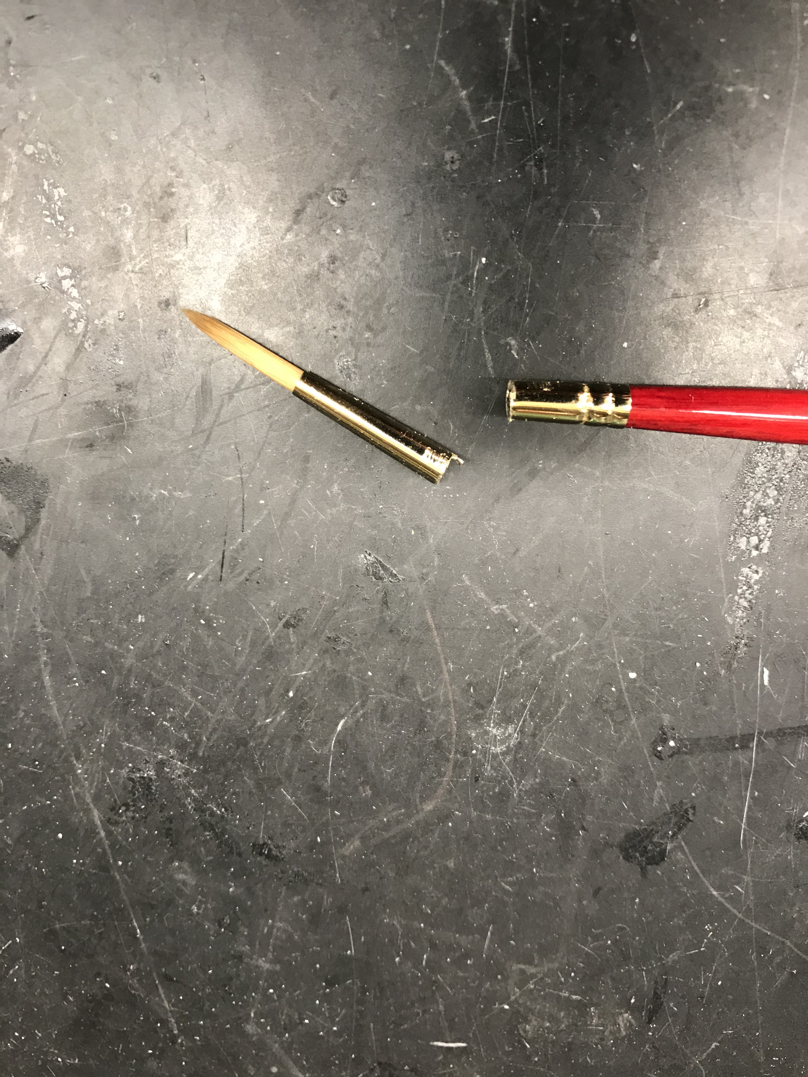
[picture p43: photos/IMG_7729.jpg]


   [Cut off the end of the paintbrush](./photos/IMG_7729.jpg)

   Correct positioning of this paintbrush is necessary for proper operation. Play with different positions of the paintbrush while the motors load and present pellets. Note that some positions of the paintbrush work well to brush off the pellets before they hit the blocker; other positions of the paintbrush are ineffective. I find that the optimal position is: paintbrush pointing straight down, tip of paintbrush just sits in the hole on the pellet presenter wheel, paintbrush glued at the tip of the blocker. As you can see in this video, the paintbrush should roll the pellets out of the holes before they hit the blocker.
   [Video](./photos/IMG_7738.MOV)
   
   With all components properly positioned, this approach is very effective. I run the rig for 5 hours each day without jams. Once you are satisfied with the positioning of the paintbrush, glue it to the blocker using Loctite and Zipkicker (you don’t need much glue, and you can break off the paintbrush and re-glue it later, if necessary).
   
   o. Some final videos demonstrating pellet loading and presentation 
   
   [Pellets loading](./photos/IMG_7739.MOV)
   
   [Pellets presented](./photos/IMG_7740.MOV)
   
15. **BUILD MOUSE HOUSE** 
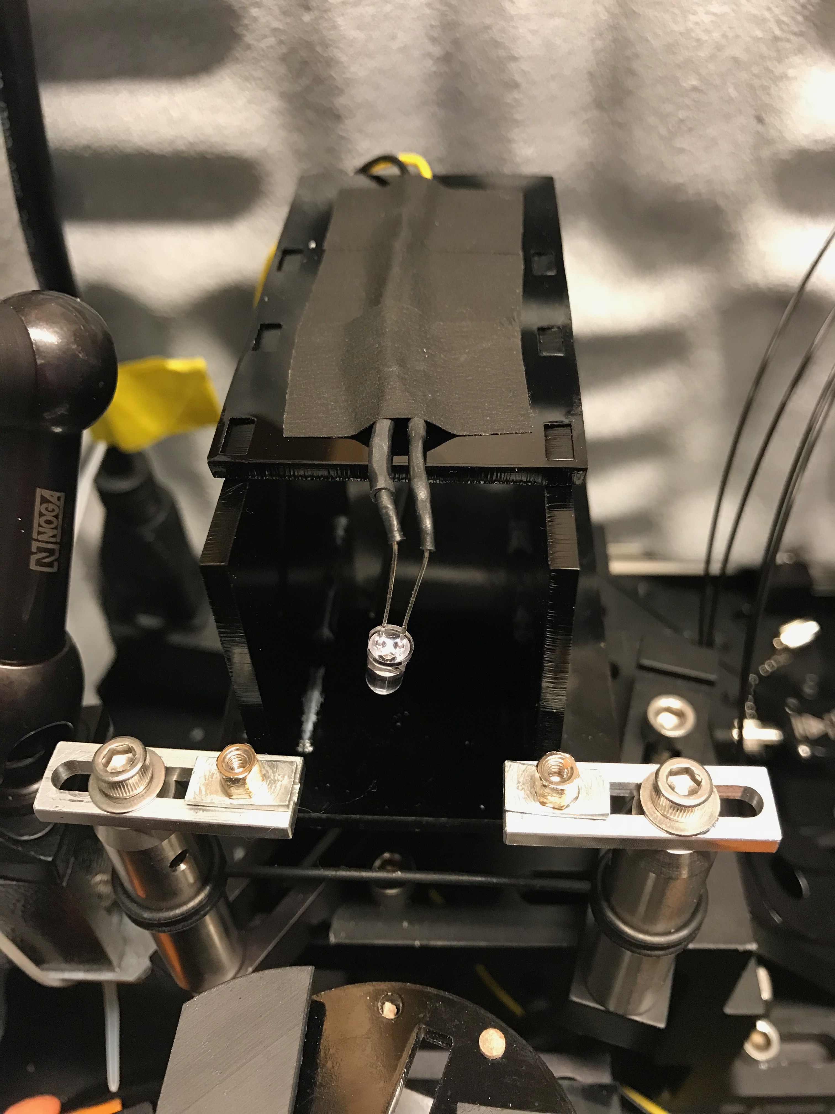
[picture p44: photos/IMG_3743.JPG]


[Mouse enclosure with distractor LED](./photos/IMG_3743.JPG)

16. Build the structure of the mouse house apparatus using ThorLabs parts.
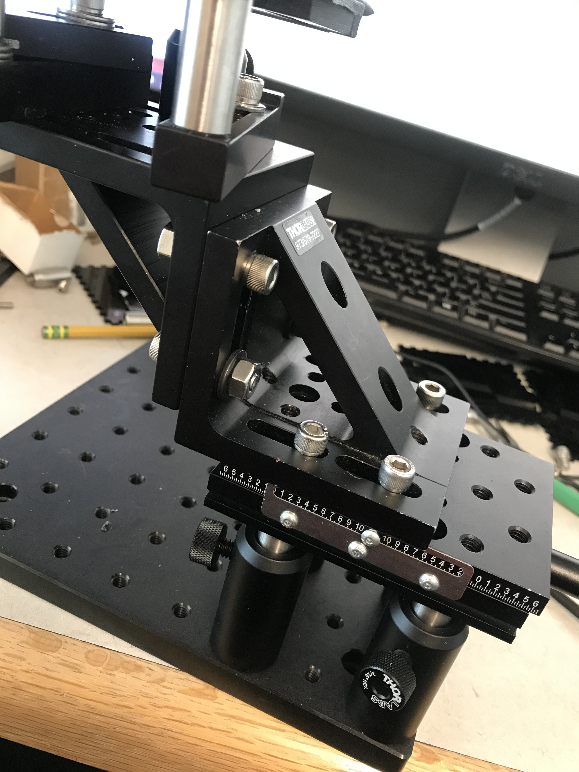
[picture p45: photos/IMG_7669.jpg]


[Something like this](./photos/IMG_7669.jpg)

Be sure that the height of the mouse house apparatus matches the height of the pellet loading apparatus.

17. Glue mouse house sides to the mouse house bottom, and tape the mouse enclosure to the base plate (BA2) at the back of the mouse house apparatus. 



[Here](./photos/IMG_7671.jpg)

18. Set up perch for mouse paws. Cut pieces of the perch to size. Attach the 3D-printed perch to 2 Thorlabs posts. Push perch to the correct height with respect to the pellet presenter wheel.


[Perch](./photos/IMG_3743.JPG)

19. Set height of mouse house. Adjust post beneath the mouse enclosure to the correct height, so that the perch and mouse enclosure bottom are at the same level. We want the mouse’s paws, which sit on the perch, to be level with the bottom of the mouse’s body, which sits within the mouse enclosure.


[Perch positioning](./photos/IMG_3743.JPG)

20. Position two halves of behavior rig. Position the mouse house apparatus and the pellet wheels apparatus with respect to each other by maneuvering breadboards. Secure the pellet wheels apparatus to the front of the McMaster behavior box frame, and secure the mouse house apparatus to the back of the behavior box frame.


[Rig from above. Note two separate breadboards for two halves of rig](./photos/IMG_3734.JPG)

21. Place Arduino and Arduino shields in protective box. Cut bottom half of the gray Arduino project box to size, so that it fits inside the black laser-cut Arduino enclosure. Place Arduino with shields onto the gray Arduino project box, trimming the posts in this box, if necessary, to accommodate the Arduino shields. Place gray project box with Arduino and shields into the laser-cut Arduino enclosure.


[See box enclosing Arduino in bottom of photo](./photos/IMG_3734.JPG)

22. **ALL THE REST OF THESE STEPS ARE OPTIONAL, DEPENDING ON YOUR EXPERIMENTAL GOALS. THESE NEXT STEPS ARE SPECIFIC TO MY EXPERIMENTS.**
I have the mice perform the reaching behavior in the dark. For my experiments, it is important that the mice cannot see, smell or whisk the food pellets, and it is important that the mice cannot hear the pellet presenter stepper motor.
23. Add infra-red filter and lens to TTL camera.
A. Add infra-red filter. The infra-red LEDs in the camera also emit in the red spectrum. To prevent leakage of this red light into the behavior box space, put an infra-red (IR) filter into the behavior camera. (We don’t want visible light to illuminate the inside of the behavior box.) Open TTL camera. Get IR filter. Cut the IR filter into a circular shape, so that the cut filter fits in the camera housing just behind the front plastic window. The filter should be big enough to fully cover the outer ring of IR LEDs. Cut a small hole at the center of the circular IR filter, matching the size of the camera lens. Place the IR filter behind the camera’s front window. and add a second lens in front of the camera’s lens. (Choose a lens that places the animal’s paws in focus, e.g., 50 mm focal length.) Close the TTL camera, screwing the front window back on. The goal of this IR filter is to be sure that red light from the infra-red (IR) LEDs does not illuminate the behavior box, because the IR LEDs in this camera have some emission in red, as well as infra-red. 
B. Add lens to TTL camera.


[Camera](./photos/IMG_3742.JPG)

24. Position camera. Attach the camera to a Thorlabs post, and position the post-holder and post on the base breadboard near the pellet wheels apparatus. Point the camera at the mouse house.


[Camera pointed at mouse house](./photos/IMG_3742.JPG)

25. Make behavior box front door. Cut holes in the front door for attachment of two hinges on the left and one metallic piece (component of the McMaster magnetic latch) on the right. Attach the door to the frame. 


[Door with hinges](./photos/IMG_3746.JPG)



[Other half of door magnetic latch on McMaster behavior box frame](./photos/IMG_3747.JPG)

26. Add the sides, bottom, back and top of the behavior box.
27. Attach the McMaster magnetic latch to hold the door shut. Attach one half of the magnetic latch to the door, and attach the other half to the behavior box frame. Door should be held shut by the magnet but easily opened by hand. Change strength of this force by adjusting overlap of 2 magnet latch pieces. 


[Half of magnetic latch on McMaster behavior box frame](./photos/IMG_3747.JPG)



[Magnetic latch on behavior box frame, with interlock wires threaded through](./photos/IMG_3752.JPG)

28. (Optional) Set up a mechanism for detecting door opening. Set up the interlock (one piece on the door, with the other piece on the behavior box frame), and thread interlock wires through the behavior box frame to the Arduino.


[Interlock (half on door, half on McMaster behavior box frame, wires threaded through frame into behavior box)](./photos/IMG_3747.JPG)



[Interlock wires entering Arduino box](./photos/IMG_3745.JPG)

29. Mask sounds: Set up speakers for noise to mask the sound of the stepper motors. Record the sound of the pellet presenter wheel. Use audio software (e.g., Audacity) to create an hour-long repetition of this noise. Save to a computer or iPad. Attach and plug in this device to speakers.


[See orange speaker beneath camera, next to stepper motor and pointed at mouse house](./photos/IMG_3742.JPG)

30. Position the small speakers as close to the pellet presenter stepper motor as possible, on either side of the mouse. These speakers will play the sound of the stepper motor continuously, thus masking the noise from the stepper motor turning.


[See orange speakers on either side of stepper motor](./photos/IMG_3734.JPG)

Record the sound of the stepper motor, and play this sound back through the speakers. Check the volume. These speakers can be quite loud without disrupting behavior. I play the masking noise at approx. 90 dB. With good sound-proofing, this is attenuated to between 60 and 70 dB just outside of the closed box. Yes, mice hear ultrasonic sounds. Empirically, it seems that the mice cannot hear or do not attend to the stepper motor noise when I play the masking sound loudly. Note that different stepper motors or configurations of the behavior box might produce ultrasonic sounds that cannot be masked by these little speakers.
Additionally, I only load pellets in a fraction of the holes on the pellet presenter wheel, so that the sound of the moving stepper motor is not perfectly correlated with pellet presentation. 

31. Add high-speed cameras and mirrors.

32. Ensure that behavior box is light-tight.

33. Make behavior box chamber anechoic. Use sound-insulating foam inside the box.

34. Make behavior box top secure but removable.

35. Power the electronic components. Solder DC barrel jacks to the powered components. Label power supplies and plug into barrel jacks. (Check that each electronic component is getting the correct power supply, e.g., 5 V or 12 V. Note that camera takes 5 V, and Arduino takes 12 V.) String power cables through the top side of the behavior box frame and into the box.



[Power cables entering through back top of box](./photos/IMG_3734.JPG)

36. Set up camera output. Solder an analog video output connector to the TTL camera output. This connector will mate with the DVR cables. 
37. Add DVR. Attach DVR to the McMaster frame.


[DVR attached to McMaster box frame](./photos/IMG_3754.JPG)

38. Hook up DVR. Hook up the camera output to the DVR input, and hook up the DVR output to the small video monitor. 
39. Configure DVR settings. 

   a. Load onto an SD card a file called “system.txt” that has one line in it reading: “F30V1S9”.
   
   b. Put this SD card into the DVR, and wait for the DVR to start up.
   
   c. Use remote control to set DVR settings to “English”, “VGA”, “Continuous” and “NTSC” (output of TTL camera is in NTSC format).
   
   d. Wait for DVR to record a short video file.
   
   e. Check video file on computer.
   
   f. DVR will now write a new movie file each time the SD card is inserted.
   
   g. Note that unplugging the DVR may cause the recording configuration to reset. (I keep the DVR plugged-in and on all the time.)

40. Load code onto Arduino. Put a micro-SD card into the Ethernet shield of the Arduino, load code onto the Arduino, and test Arduino. May need to change “chip select” pin for writing to micro-SD card. For example, Arduino Ethernet shield with W5500 chip set will use “chip select” pin 2, whereas Arduino Ethernet shield 2 will use “chip select” pin 4.
41. Wire up a distractor LED. Hook up the Arduino digital output to the LED positive lead. Hook up a resistor to the LED negative lead, then hook up the other end of the resistor to Arduino ground.


[Distractor LED on top of mouse enclosure](./photos/IMG_3743.JPG)

42. Cover LEDs on small speakers to prevent illumination of inside of behavior box.
43. Trim whiskers.
44. Mask smell. The mice can smell the pellets approaching. There are 2 options here. Option 1. Insert a small tray beneath the mouse. Fill this tray with fresh pellets. Change these pellets frequently. These pellets mask the smell of pellets on the pellet presenter wheel. Option 2. Use a small CPU fan pointed at the mouse’s face to move air around within the behavior box. This will prevent the animals from localizing the approaching pellet based on smell. I now use Option 2 exclusively.
45. If doing optogenetic stimulation, use a mating sleeve covered in black tape and clay to fully block the exit of optogenetic light from the fiber and mating sleeve into the behavior box space.
46. (Optional) Raise the behavior rig for easier cleaning. I raised all components and inserted removable drawers at the bottom of the rig, so that dropped pellets could be collected in the drawers and easily thrown away.

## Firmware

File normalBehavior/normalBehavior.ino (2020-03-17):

#include <Wire.h>
#include <Adafruit_MotorShield.h>
#include "utility/Adafruit_MS_PWMServoDriver.h"
#include <SPI.h>
#include <SD.h>
#include <EEPROM.h>

const long day = 86400000; // 86400000 milliseconds in a day
const long hour = 3600000; // 3600000 milliseconds in an hour
const long minute = 60000; // 60000 milliseconds in a minute
const long second = 1000; // 1000 milliseconds in a second
const uint8_t I2Caddress = 0x60; // use 0x60 as default address
const int chipSelect = 4;

Adafruit_MotorShield AFMS = Adafruit_MotorShield(I2Caddress);

String serialStringOut(String outString, String appendString)
{
  Serial.print(outString);
  appendString += outString;
  return appendString;

}

String time()
{
  long timeNow = millis();
  String outString = "";
  int days = timeNow / day ; //number of days
  int hours = (timeNow % day) / hour; //the remainder from days division (in milliseconds) divided by hours, this gives the full hours
  int minutes = ((timeNow % day) % hour) / minute ; //and so on...
  int seconds = (((timeNow % day) % hour) % minute) / second;

  // digital clock display of current time
  outString = serialStringOut(String(days, DEC), outString);
  outString = serialStringOut(printDigits(hours), outString);
  outString = serialStringOut(printDigits(minutes), outString);
  outString = serialStringOut(printDigits(seconds), outString);
  outString = serialStringOut("\r\n", outString);
  return outString;
}

String printDigits(byte digits)
{
  String outString = "";

  // utility function for digital clock display: prints colon and leading 0
  outString = serialStringOut(":", outString);
  if (digits < 10)
  {
    outString = serialStringOut("0", outString);
  }
  outString = serialStringOut(String(digits, DEC), outString);
  return outString;
}

class DataCard
{

    String dataFile;

  public:
    DataCard(int chpselect, String fileName)
    {
      Serial.print("Initializing SD card ...");
      // see if the card is present and can be initialized
      if (!SD.begin(chpselect))
      {
        Serial.println("Card failed or not present");
        return;
      }
      Serial.println("Card initialized");
      dataFile = fileName;
    }

    void Update(String dataString)
    {
      // open the file
      File data = SD.open(dataFile, FILE_WRITE);
      // if file is available, write to it
      if (data)
      {
        data.println(dataString);
        data.close();
        // print to serial port as well
        //      Serial.println(dataString);
      } else
      {
        Serial.println("Error open SD file");
        Serial.print(">");
        Serial.print(millis());
        Serial.print(">");
        time();
      }
    }
};

DataCard outSD(chipSelect, "output.txt");

class StepperDisk
{
    Adafruit_StepperMotor *myStepper;
    long stepSize; // distance for stepper motor to move per trial
    long updateDelay; // time between steps
    int stepsPerRevolution; // number of steps per revolution
    long motorRPM; // motor speed
    unsigned long lastUpdate; // last update of position
    int stepsSoFar = 0; // number of steps moved on this trial
    int writeCode;
    long delayBeforeTurn = 0; // in ms, delay before movement onset, triggered on trial start
    long trialOnset = 0;
    boolean accomplishedTurn = false;
    boolean goesForward = true;
    int countLoaderSteps = 0;
    long startOfLoad = 0; // time in ms when loader turn begins

  public:

    StepperDisk(int nSteps, int whichMotor, int eventLabel, boolean forwardDirection)
    {
      // Connect a stepper motor with nSteps per revolution in position whichMotor
      myStepper = AFMS.getStepper(nSteps, whichMotor);
      stepsPerRevolution = nSteps;
      writeCode = eventLabel;
      goesForward = forwardDirection;
    }

    void SetAngle(int nSteps)
    {
      if (goesForward == true)
      {
        myStepper->step(nSteps, FORWARD, MICROSTEP);
      } else
      {
        myStepper->step(nSteps, BACKWARD, MICROSTEP);
      }
    }

    void SetSpeed(long rpm)
    {
      myStepper->setSpeed(rpm); // in rotations per minute
      motorRPM = rpm;
    }


    void Update(long currStepSize, long waitToTurn, boolean trialStarting, boolean doMove)
    {
      long timeFromLoad; 
      if (doMove == false) // don't move wheel
      {
        return;
      }
      if (trialStarting == true) // start of a new trial
      {
        // set goal distance for motor to move on this trial
        stepSize = currStepSize;
        // at given rpm speed, calculate update delay
        updateDelay = (1 / stepsPerRevolution) * (60 / motorRPM); // in seconds
        stepsSoFar = 0; // reset to zero
        // set delay before motor starts turning
        delayBeforeTurn = waitToTurn;
        trialOnset = millis();
        accomplishedTurn = false;
      }
      if ((millis() - trialOnset) > delayBeforeTurn) // time to start turning
      {
        if ((millis() - lastUpdate) > updateDelay) // time to update
        {
          lastUpdate = millis();
          if (stepsSoFar < stepSize)
          {
            if (stepsSoFar == 0) // starting turn
            {
              String outString = "";
              outString = serialStringOut(String(writeCode), outString);
              outString = serialStringOut(">S>", outString);
              outString = serialStringOut(String(millis()), outString);
              outString = serialStringOut("\r\n", outString);
              outSD.Update(outString);
            }
            if (goesForward == true)
            {
              myStepper->step(1, FORWARD, MICROSTEP);
            } else
            {
              myStepper->step(1, BACKWARD, MICROSTEP);
            }
            stepsSoFar += 1; // moved one more step
          } else if ((stepsSoFar >= stepSize) && (accomplishedTurn == false)) // ending presenting wheel turn or finishing loader turn
          {
            if (currStepSize == 1) // this is the loader wheel
            {
              if (countLoaderSteps<6) // haven't yet finished load
              {
                timeFromLoad = millis() - startOfLoad;
                if (timeFromLoad > 500) // 500 ms delay between loader steps
                { 
                  if (goesForward == true)
                  {
                    myStepper->step(1, FORWARD, INTERLEAVE);
                  } else
                  {
                    myStepper->step(1, BACKWARD, INTERLEAVE);
                  }
                  countLoaderSteps = countLoaderSteps+1;
                  startOfLoad=millis();
                  if (countLoaderSteps == 6)
                  {
                    countLoaderSteps = 0; // reset to 0
                    accomplishedTurn = true; // finished loader turn
                  }
                }
              }
            } 
          }
        }
      }
    }
};

class FlashOnce
{

    int ledPin; // analog output pin number
    long OnTime; // milliseconds of on-time
    long OffTime; // milliseconds of off-time
    int ledState; // led state
    unsigned long previousMillis; // stores last time LED was updated
    boolean didOnce = false; // whether already flashed once
    int writeCode;
    long currDelay; // delay for this trial between wheel finishing turning and cue turning on

  public:
    FlashOnce(int pin, long on, long off, int eventLabel)
    {
      ledPin = pin;
      pinMode(ledPin, OUTPUT);
      OnTime = on;
      OffTime = off;
      ledState = LOW; // start off
      digitalWrite(ledPin, ledState); // Update the actual LED
      previousMillis = 0;
      writeCode = eventLabel;
    }

    void Update(boolean trialStarting, boolean turnCueOn)
    {
      unsigned long currentMillis = millis();
      if (turnCueOn == false) // don't turn cue on
      {
        return;
      }
      if (trialStarting == true)
      {
        // re-initialize so can turn on again
        didOnce = false;
        // check that LED is off
        ledState = LOW;
        digitalWrite(ledPin, ledState); // Update the actual LED
        previousMillis = currentMillis;
      }
      if ((ledState == HIGH) && (currentMillis - previousMillis >= OnTime))
      {
        ledState = LOW; // Turn it off
        previousMillis = currentMillis; // Remember the time
        digitalWrite(ledPin, ledState); // Update the actual LED
        String outString = "";
        outString = serialStringOut(String(writeCode), outString);
        outString = serialStringOut(">E>", outString);
        outString = serialStringOut(String(millis()), outString);
        outString = serialStringOut("\r\n", outString);
        //      outString = serialStringOut(">", outString);
        //      outString = serialStringOut(time(), outString);
        outSD.Update(outString);
      }
      else if ((ledState == LOW) && (currentMillis - previousMillis >= OffTime) && (didOnce == false)) // Haven't yet turned LED on
      {
        ledState = HIGH; // Turn it on
        previousMillis = currentMillis; // Remember the time
        digitalWrite(ledPin, ledState); // Update the actual LED
        String outString = "";
        outString = serialStringOut(String(writeCode), outString);
        outString = serialStringOut(">S>", outString);
        outString = serialStringOut(String(millis()), outString);
        outString = serialStringOut("\r\n", outString);
        //      outString = serialStringOut(">", outString);
        //      outString = serialStringOut(time(), outString);
        outSD.Update(outString);
        didOnce = true; // Save that turned on once
      }
    }
};
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

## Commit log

2020-03-17 Rig for dispensing and presenting pellets
    Custom hardware for behavior rig to maneuver mouse food pellets
    [chute_and_blocker.ipt, chute_and_blocker.stl, pellet_loader_conical_piece.ipt, pellet_loader_conical_piece.stl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]
2020-03-17 parts list as csv
    [parts_list.csv]
2020-03-17 added arduino code
